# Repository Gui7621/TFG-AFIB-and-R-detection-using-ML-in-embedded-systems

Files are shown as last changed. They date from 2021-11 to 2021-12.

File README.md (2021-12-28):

# AFIB And SR Detection Using ML In Embedded Systemns

<p align="center"> 
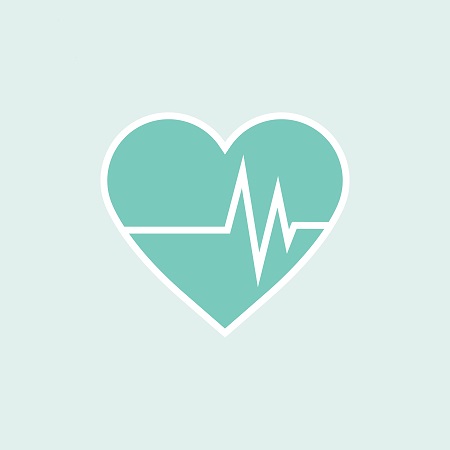
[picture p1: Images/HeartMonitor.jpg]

</p>

The project data shared in this repository has been divided into certain folders that involve different steps performed in TFG.

The first one (R Peak Detection Algorithm) has the Python file of the algorithm built along with the tests done to attest to its functionality.

The second folder (Schematic file in Fritzing) has the file to be edited in Fritzing with the schematic on the protoboard of the assembled prototype.

The "Jupyter Notebook Files" folder contains several Python files that show the entire development of the machine learning project, from working with the database including filtering and normalizing records to building and testing the neural model.

The folder "Model classifications for ECG data sampled in SimMan Simulator" contains the Excel files containing the results of the model classifications for the exams performed in SimMan.

The folder "ECG data sampled in SimMan Simulator" has some Excel files that contain RS and FA ECG records collected from SimMan, where some were used to test the model in Jupyter Notebook files.

The sixth folder (Link of the project with the final model in Edge Impulse) contains a txt file with the link to the public project in Edge Impulse that has the neural model used to make the inference in ESP32. There you can also check the model's training and test results, as well as its input data, which are precisely the individual heartbeats.

Finally, the "Program in C++" folder has the .ino file of the final program used to make the inference of the model in C++ in ESP32, including all steps of sampling the cardiac signal, data processing, obtaining the R peaks and the individual heartbeats to the final 10s model and exam scores.

<p align="center"> 
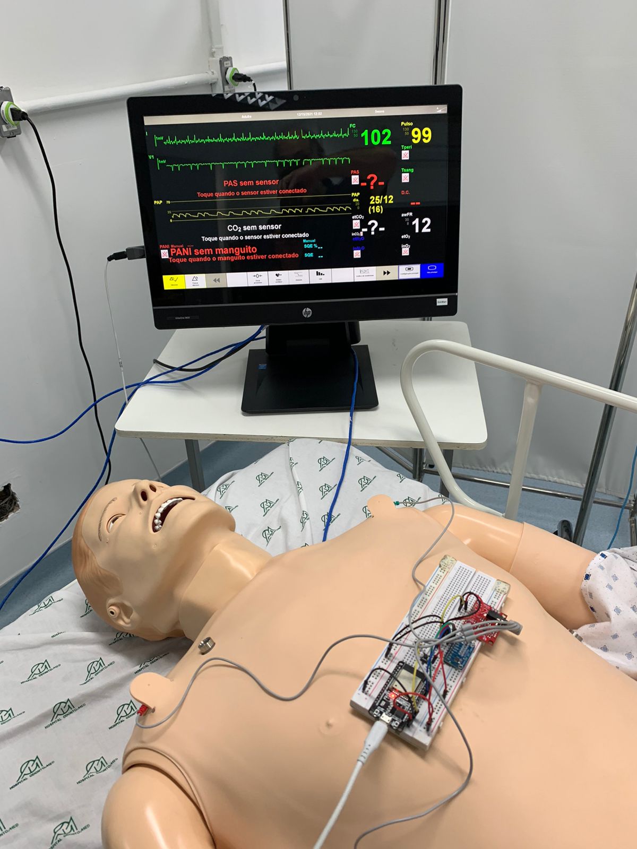
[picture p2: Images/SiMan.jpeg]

</p>

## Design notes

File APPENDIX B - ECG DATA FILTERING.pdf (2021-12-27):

## APPENDIX B - ECG DATA FILTERING

An ECG signal is made up of several sources. Recording is done using electrodes on the skin, which capture more than just the electrical activity of the heart. The primary electrical components captured are signals from the myocardium, muscles, skin-electrode interface and external interference.

The most common frequencies of important components on the ECG are:

Heart rate: 0.67 - 5 Hz (which equates to: 40 - 300 bpm)

P wave: 0,67 - 5 Hz

QRS: 10 - 30 Hz

T wave: 1 - 7 Hz

Meanwhile, the common frequencies of the medical apparatus and noise on the ECG are:

Muscle movement: 5 - 50 Hz

Respiration: 0,12 - 0,5 Hz (eg, 8 - 30 bpm)

Power line interference: 50 or 60 Hz

Other electrical: typically > 10 Hz (derived from muscle stimulators, strong magnetic fields and pacemakers with impedance monitoring)

When filtering out any biomedical signal, care must be taken not to alter the desired information in any way.

A big concern is how the QRS complex influences the filter's output; for the filter, it often represents a big unwanted boost. The possible distortion caused by the filter must be carefully quantified.

Filtering on an ECG, in principle, can be done in two steps, that is, with the application of 2 filters: a high-pass filter and a low-pass filter. The high-pass filter removes low-frequency signals (that is, only the highest frequencies can pass), and the low-pass filters remove highfrequency signals. High-pass and low-pass filters together are known as a band-pass filter, literally allowing only a certain frequency band to pass.

All filters introduce distortion into the resulting output signal. This distortion can be in amplitude or phase. Filters found in heart monitors need to be real-time and therefore cannot tolerate delays. Because of this, the filter output exhibits non-linear characteristics due to its shorter required delays. Basically, they distort different frequencies, causing phase distortion. If filters were applied during post-processing, where real-time output of the signal is unnecessary, the design of these filters can be linear, which minimizes phase distortion.

Low-pass filters on the ECG are used to remove high frequency muscle noise and especially electrical line interference noise. Analog low-pass filtering has a noticeable effect on the QRS complex, epsilon, and J waves, but does not alter the repolarization signals.

High-pass filters remove low-frequency components such as motion noise, breathing variation, and baseline wobble. Unlike low-pass filters, analog high-pass filters do not attenuate the signal too much. However, analog high-pass filters suffer from the phase shift that affects the first 5 to 10 harmonics of the signal. This means that a 0.5 Hz high-pass filter, which is a lower frequency than that produced by the myocardium, can still affect frequencies up to 5 Hz. To reduce this effect, a higher order filter is used, where frequencies near and above the cutoff frequency have virtually no attenuation.

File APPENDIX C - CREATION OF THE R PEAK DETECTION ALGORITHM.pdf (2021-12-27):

## APPENDIX C - CREATION OF THE R PEAK DETECTION ALGORITHM

An important detail in the creation of this algorithm was the fact that it did not need to operate in real time, that is, the R peaks were identified during the ECG measurement. This happens because, since the classification of the machine learning model and generation of images of heartbeats requires that the signal is already ready, this can also be done with the algorithm. This algorithm is used both in the preparation of the signal for training the model, as well as in the microcontroller for the functioning of the prototype.

With that, the algorithm works as follows: Considering that the ECG record is sampled at 100Hz for 10s, which is the standard adopted by the German database, firstly, the highest value of the 1000 points that exist in the record is found. Then, the reference value of the algorithm is assigned as being half of the highest value found previously. The functioning of this assignment directly depends on the filtering performed in the previous step, as it will be possible to remove certain noisy components that distort the signal and make it oscillate, mainly baseband noise. With filtering, the record is approximately centered at 0 and with R peaks with similar amplitudes.

In this way, all the points of the signal in question are traversed, and if any of them is greater than the calculated reference value, the next step in the algorithm is evaluated, where the 5 points following the one identified as being greater are evaluated. than the reference value, and then determine which is the greater among them. This will correspond to an R peak. It then saves both the sample value of this R peak as well as the position of this sample in the signal as a whole.

The reason for evaluating the additional 5 points is to ensure that you get the highest value of the QRS complex according to the 100Hz sampling frequency used. As one can have values greater than the reference value within the QRS complex after the R peak, it is necessary to skip a certain number of samples after its identification. Knowing that heart rate varies within a range of 40 bpm to 200 bpm, it is possible to calculate the maximum number of samples without the occurrence of an R peak as a function of frequency, given by: :

6

2 = 6∗1

2 =
30. Therefore, once an R peak is found, 30 samples of signal analysis can be skipped without

the possibility of identifying another R peak. This process is carried out during the entire length of the signal.

Consequently, it is concluded that the R peak detection algorithm needs to have the signal already sampled. Its operation consists of traversing the 10s ECG record, looking for points above a reference value within a certain range, where the largest sample in this region is an R peak. The algorithm, when tested, showed a huge efficiency when compared to the application of other similar methods, in addition to providing faster execution.

The tests that were carried out in order to verify the performance of the algorithm consisted of comparing the results obtained by the algorithm created from the signals captured from the SimMan simulator with the results considering the same input signals using a Python extension tool known as BioSPPy, which can be accessed from the following link: https://github.com/PIA-Group/BioSPPy.

This extension brings together several signal processing and pattern recognition methods aimed at analyzing biosignals, having support for several biological signals such as ECG, EEG, EMG and respiration. Its operation includes several tried and tested signal analysis techniques such as filtering, frequency analysis and R peak detection, which in turn was created from the
study of P.S. Hamilton in the article “Open Source ECG Analysis Software Documentation”.

As for the test itself, four base signals were used, composed of ECG recordings with SR with and without noise and in an analogous way for AFIB. By applying the BioSPPy algorithm, a total of 337 R peaks were detected.

After that, running the algorithm created in this article, the detection of each of the 337 R peaks identified in the previous algorithm was observed, as well as some extra indications in the AFIB signals, where when visually verifying the signal actually consisted of R peaks.

Therefore, the created algorithm was able to correctly identify the R peaks of SR and AFIB signals in comparison with the BioSPPy algorithm, as well as finding R peaks in AFIB signals that went unnoticed by the reference algorithm.

The tests and their results can be accessed in the project repository, more specifically, in the folder reserved for the development of this algorithm.

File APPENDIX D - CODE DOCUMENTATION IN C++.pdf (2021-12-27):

## APPENDIX D - CODE DOCUMENTATION IN C++

Code development in C++:

For the development of the embedded code, we wanted to reapply all the steps carried out in the training of the model written in Python, as this is extremely important for the model to be able to perform well and work under the same conditions in which it was created and trained;

In this way, the code development in C++ was divided into steps that would make the work easier and could help maintain the same conditions that were applied at a high level with Python. The chosen steps were then: data acquisition and data processing in real time, separation of beats, introduction of the signal in the model and classification. All these steps will be opened and worked on below.

Acquisition and training of data in real time:

In the acquisition step, the Adafruit_ADS1x15 library was used to configure and read the ADC, where 3 interrupts were used to manage the code's operation. The first interrupt monitored the change in a push button, and triggers a debounce routine to confirm that the switch was pressed. Then, two interrupts were triggered, in which one is triggered every 0.01s and is responsible for releasing the data acquisition flag and keeping the sampling frequency at 100 Hz, and a second interrupt is responsible for signaling the end of the data acquisition time which is 10s.

In the data processing process in Python, the library used was scipy, so that in Python two filters were defined: a high-pass with a cut-off frequency of 0.5 Hz and a low-pass with a cutoff frequency of 41 Hz In order to replicate data processing in C++, the libfilter library was used, which has very similar implementations to those used in the process carried out at a high level for model training, where this library enabled the creation of a low-pass filter of 3rd order with a cutoff frequency of 41 Hz, and a 2nd order high pass filter with a cutoff frequency of 0.5 Hz, thus forming a bandpass filter that is applied in real time as the data is acquired from the ADC.

All read and processed data were stored in an array declared as static in the microcontroller's memory that is created at the time of processor initialization. These data were stored to be used in the following steps, for the creation of data that are delivered with the objective that the classification of the model is carried out.

Separation of heartbeats:

In the step of separating the heartbeats in Python, the biosppy library was used to normalize the heartbeats and create the images, where at first we tried to make a direct translation of this library to C++, which was not very practical, leading to the creation of our own code for peak detection that was first applied in Python and then translated to C++, so with a few minor adaptations this routine managed to be translated and tested inside the microcontroller.

After all the signal peaks are identified, it goes to the heartbeat separation step. With the QRS point indices in hand, it is possible to assemble a matrix containing all the heartbeats present in the signal, taking 60 points in front of the QRS peak and 40 points behind the QRS peak, thus forming the heartbeats. Here, care is only taken to avoid picking up points that were on the edge of the signal, which can configure signals without correct identification.

Input of the signal in the model and final classification:

In this step, the deployment is carried out using the Edge Impulse tool, which was responsible for optimizing and converting the model, thus reducing both the memory expenditure used by the model and the processing expenditure necessary for it to be able to run on a processor with fewer resources, such as embedded processors. In exchange for that, the model loses some of its precision, which in the case of this project proved to be imperceptible.

After processing the model by the tool, a library is obtained with the model application ready, where both the model and some tools that were also delivered by Edge Impulse are extracted, such as the feature vector where the data that will be processed is introduced. by the model. With this in mind, we went through the classification stage, where the valid heartbeats were introduced in the features vector provided by the Edge Impulse library.

From there, the classification function is called, which will analyze and classify each heartbeat individually, so that after classifying all the beats, a comparison is made between the number of heartbeats classified as AFIB and SR. The one with the highest number of ratings is indicated as the heart rhythm identified in the 10s exam.

Trobleshoot:

Possible improvements of the work carried out would be: improvement in the quality of the filters performed, creation of a model capable of detecting a greater number of arrhythmias, in addition to an increase in the sampling rate, which would make it possible to acquire more accurate data with a smaller spacing between samples.

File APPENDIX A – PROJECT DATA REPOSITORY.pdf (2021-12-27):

## APPENDIX A – PROJECT DATA REPOSITORY

The link to the repository that contains the Jupyter Notebook programs with the functions described in this article, along with the neural model developed on the Edge Impulse platform, as well as the ECG data obtained from the measurements on the simulator SimMan is given by:

https://github.com/Gui7621/TFG-AFIB_and_SR_detection_using_ML_in_embedded_systems

In addition, the adapted database from the original German PTB-XL database is also made available, where only data related to normal sinus rhythm and atrial fibrillation were filtered. This database, which was used as a reference in the programs created in Python, can be accessed through the following link:

https://zenodo.org/record/5711347#.YZa1c07MLIW

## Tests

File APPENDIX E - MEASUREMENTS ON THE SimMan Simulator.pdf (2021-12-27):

## APPENDIX E - MEASUREMENTS ON THE SimMan SIMULATOR

The prototype developed to carry out measurements on the simulator is composed of the following components:

a) ESP32:

Development board with 30 pins of which 25 are digital input/output, Clock up to 240MHz, 520KB RAM memory and 4MB FLASH memory.

b) AD8232 cardiac monitoring sensor:

Capable of measuring the electrical activity of the heart which can be mapped as an ECG and generated as an analog reading. This sensor performs a pre-filtering in order to clean the signal from possible noise.

c) Cable with electrode pads.

They are used to connect the electrodes to the AD8232 sensor.

d) ECG electrodes with a disposable surface.

These are the devices that connect the patient with the cardiac sensor, where electrical information is obtained for printing and analyzing the ECG.

e) Protoboard and jumpers.

They carry out the electrical connections of the prototype components.

f) USB cable type A-B:

It has the function of connecting the computer with a digital output from ESP32, in order to allow the sending of data worked on the development board to the computer for future analysis.

g) ADS1115 analog-digital converter:

Its purpose is to convert the analog signal from the heart monitor to digital in order to be treated by ESP32. It has 16-bit precision at 860 samples/second. Its interface is via I2C protocol. Furthermore, it can be configured as 4 single-ended input channels or two differential channels. Its use in the prototype was necessary because the ESP32's A/D converter does not have the required quality expected for sampling and analog signal conversion.

h) Tactile key with 4 terminals:

Its function is to indicate the start of recording an exam when it is pressed. It works by sending to a digital pin of ESP32 a logic state that indicates whether it was pressed or not. The debounce technique was used in order to avoid possible problems with undefined transitions in moments of pressure due to mechanical or physical failures.

The main connections between the components listed above are described below:

Connecting the AD8232 heart monitor to the ADS1115:

Table I – AD8232 Heart Monitor Connections with ADS1115 Component

Pin name on AD8232 board | Pin functions | Connection on ADS1115
GND | Ground | Ground
3.3V | 3.3V power | 3.3V
OUTPUT | output analog signal | A0 pin
LO - | lead detection - | NC
LO + | lead detection + | NC
SDN | turn off | NC

Connection of ADS1115 analog-digital converter with ESP32:

Table II – ADS1115 Analog-to-Digital Converter Connections with ESP32

ADS1115 | Connection on ESP32
GND | Ground
3.3V | 3.3V
SCL | SCL pin (22)
SDA | DAS pin (21)
ADDR | Ground
ALRT | NC
A0 | NC
A1 | NC
A2 | NC
A3 | NC

The schematic with the connection between the three components mentioned above is shown below:

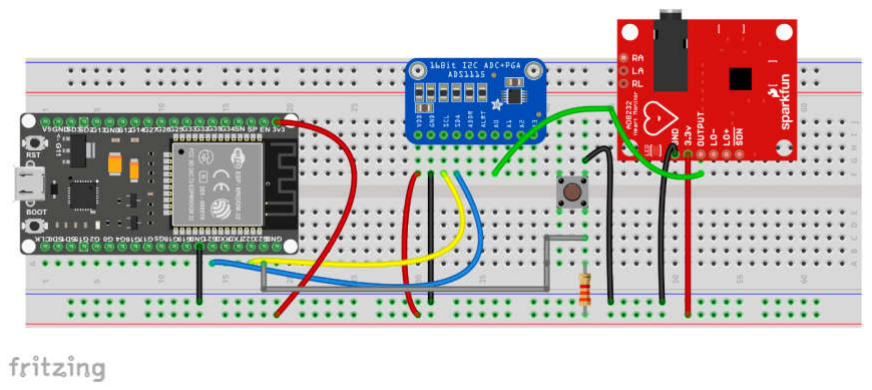
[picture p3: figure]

Fig. 1: Prototype assembly schematic. Source: Fritzing, 2021.

The connection of the electrode pads with the signals to be sampled from the body according to the type I lead is given by:

Table III – Connections of the electrode pads to the body

Cable color | Signal
Green | LA (Left Arm)
Red | RA (Right Arm)
Yellow | RL (Right Leg)

The layout of the type I lead reading in the human body is exemplified in the image below:

Fig. 2: Positioning the electrode pads on the human body. Source: Author, 2021.

The arrangement of connections already in the simulator is shown in the figures below:

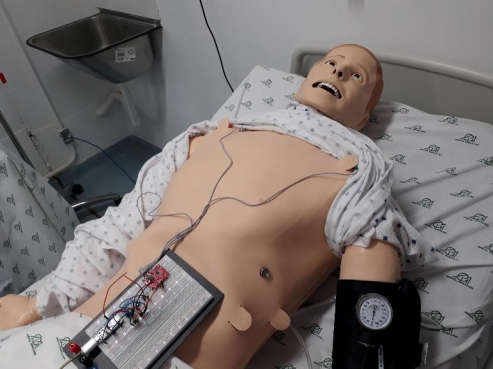
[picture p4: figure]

Fig. 3: Prototype layout in SimMan. Source: Author, 2021.

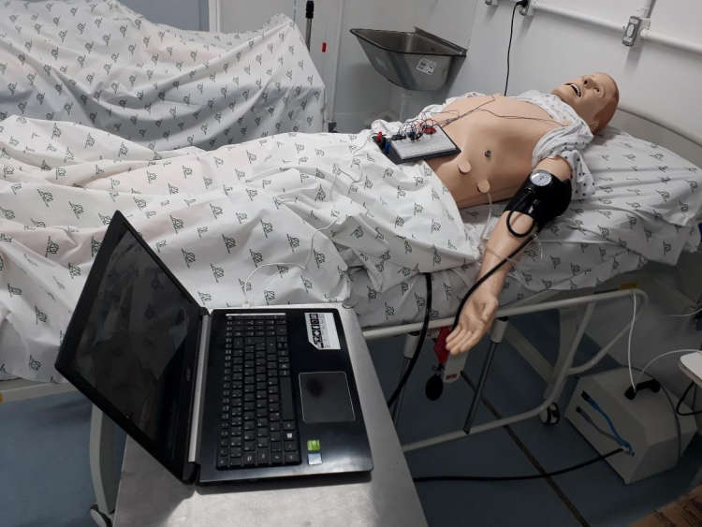
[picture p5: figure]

Fig. 4: Prototype layout in SimMan. Source: Author, 2021.

As described in the article, once the prototype had already been assembled, several AFIB and SR signals were started to be applied to the simulator, with or without noise. Shown below are some of these already filtered signals obtained.

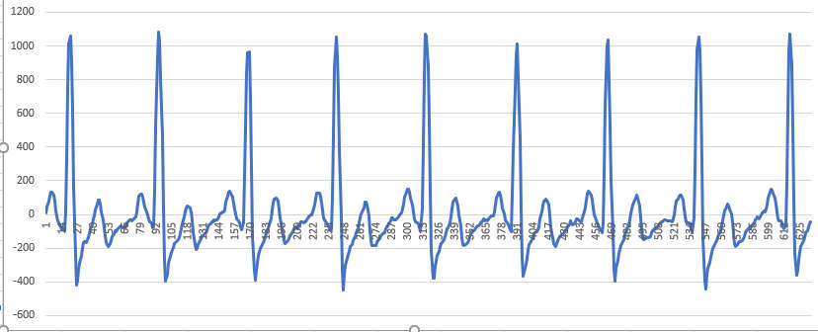
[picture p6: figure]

Fig. 5: Signal from a noiseless SR ECG record. Source: Author, 2021.

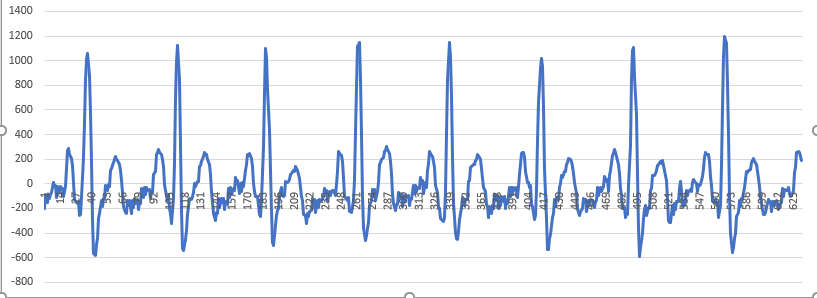
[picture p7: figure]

Fig. 6: Signal from a noisy SR ECG record. Source: Author, 2021.

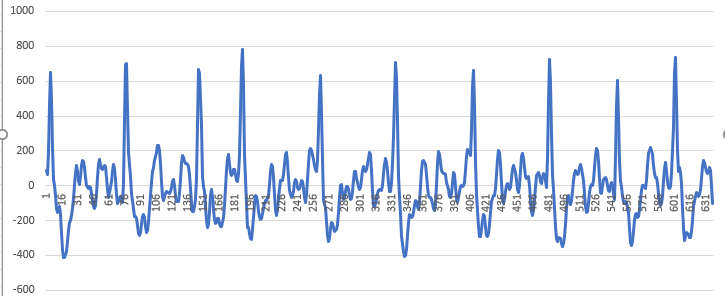
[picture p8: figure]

Fig. 7: Signal from a noiseless AFIB ECG record. Source: Author, 2021.

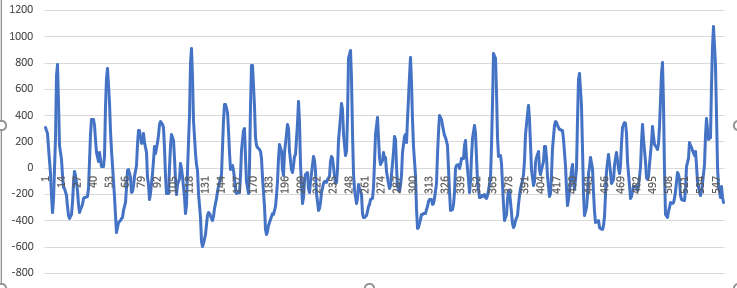
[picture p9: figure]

Fig. 8: Signal from a noisy AFIB ECG record. Source: Author, 2021.

About the classifications themselves, it is attested that they last an average of 8ms, as shown in the image below, that is, this is the duration of the model inference. This constant is close to that estimated by Edge Impulse, which was 10ms.

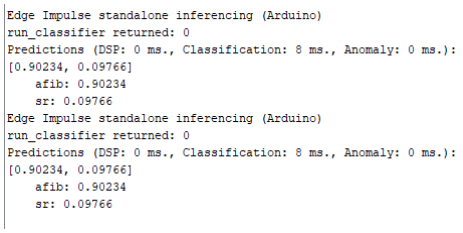
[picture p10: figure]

Fig. 9: Records of model classification parameters. Source: Author, 2021.

Finally, an idealization of how it is expected in the future to transform the prototype into a single board capable of performing both the sampling, treatment, classification and display of data and results is presented below. It will have many of the components mentioned above for the construction of the original prototype with the addition of the display, although the ESP32 will be replaced by a microcontroller with an even smaller size, containing just what is necessary to run the machine learning model and treatment of the ECG data. There is also the addition of an external battery, in order to make the ECG measurement safer, since it will not be necessary to connect directly to the electrical network.

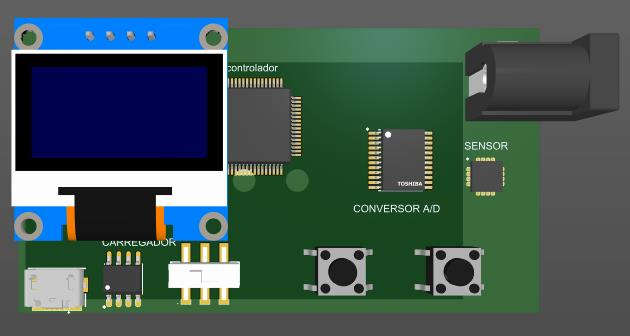
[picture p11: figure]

Fig. 10: Idealization of the final prototype of the project (front of the board). Source: Author, 2021.

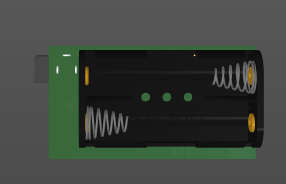
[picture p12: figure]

Fig. 11: Idealization of the final prototype of the project (behind the board). Source: Author, 2021.

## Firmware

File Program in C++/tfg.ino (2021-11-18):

/***********************************************
  Includes.
***********************************************/
#include <Adafruit_ADS1X15.h>
#include <Wire.h>
#include <movingAvg.h>
#include <filters.h>
#include <filters_defs.h>
#include <stdio.h>
#include <stdlib.h>
#include <stdint.h>
#include <ecg_project_test_1_inferencing.h>


/***********************************************
  Defines.
***********************************************/
#define SAMPLE_RATE_US 10000 //Limitado a 128 pela biblioteca Adafruit_ADS1X15 para alterar use a fução ConfigSampleRate(uint rate) com os valores disponíveis no enum sampleRate.
#define DEBOUNCE_TIME_MS 25
#define MULTIPLIER_VALUE 0.1875F
#define MOVING_AVG_WINDOW_SIZE 3
#define BUTTON_PIN 2
#define EXAM_DURATION_US 1000
#define MAX_SIGNAL_POINTS 1000
#define MAX_HEARTBEATS_CAPTURED 15
#define MAX_HEARTBEAT_IMAGE_SIZE 100
/***********************************************
  Variáveis.
***********************************************/
//Variáveis do Timer de leitura do ADC.
volatile bool timerFlagAdc;
hw_timer_t * timer0 = NULL;
portMUX_TYPE timerMux0 = portMUX_INITIALIZER_UNLOCKED;

//Variáveis do Timer de controle do tempo do exame.
volatile bool timerFlagExamFinished;
volatile int count;    // Trigger
hw_timer_t * timer1 = NULL;
portMUX_TYPE timerMux1 = portMUX_INITIALIZER_UNLOCKED;

//Variáveis dos Filtros
const float samplingTime = 0.01;                            //Sampling time em segundos.
const float cutoffFreqHigh   = 0.5;                                              //Frequência de corte em Hz.
const float cutoffFreqLow   = 41.0;                                              //Frequência de corte em Hz.
Filter fhp(cutoffFreqHigh, samplingTime, IIR::ORDER::OD2, IIR::TYPE::HIGHPASS);
IIR::ORDER  order_low  = IIR::ORDER::OD3;                                           // Order (OD1 to OD4)
Filter f(cutoffFreqLow, samplingTime, order_low);
movingAvg avgValue(1);
const float multiplier = 0.1875F;

//Variáveis do ADC.
Adafruit_ADS1115 ads;
enum sampleRate {
  SPS8 = 0x0000, //< 8 amostras por segundo.
  SPS16 = 0x0020, //< 16 amostras por segundo.
  SPS32 = 0x0040, //< 32 amostras por segundo.
  SPS64 = 0x0060, //< 64 amostras por segundo.
  SPS128 = 0x0080, //< 128 amostras por segundo(padrão).
  SPS250 = 0x00A0, //< 250 samples amostras por segundo.
  SPS475 = 0x00C0, //< 475 amostras por segundo.
  SPS860 = 0x00E0, //< 860 amostras por segundo.
};

//Variáveis do Botão.
const uint button = BUTTON_PIN;         //Botão configurado no pino2.
volatile boolean buttonFlag;

//Variáveis para a criação de HeartBeats.
int SignalFiltred[MAX_SIGNAL_POINTS];
int SignalImages[MAX_HEARTBEATS_CAPTURED][MAX_HEARTBEAT_IMAGE_SIZE];
float SignalImagesNormalized[MAX_HEARTBEATS_CAPTURED][MAX_HEARTBEAT_IMAGE_SIZE];
int SignalMaxPointsIndex[MAX_SIGNAL_POINTS];
int signalIndex;

//Variáveis para controle da máquina de estados.
uint state = 1;
bool examStart;
enum states {ms_wait, ms_readingButton, ms_automaticInitiation, ms_starting, ms_collectingData, ms_examFinished, ms_buldingImage, ms_sendingImageToClassification};

//Variáveis para classificação.
static int AFIB_cont = 0;
static int SR_cont = 0;
int zeroCountClassifcationImage = 0;
static float features[100] = {
  // copy raw features here (for example from the 'Live classification' page)
  // see https://docs.edgeimpulse.com/docs/running-your-impulse-arduino
};

/***********************************************
  Definição de funções.
***********************************************/
//Funções do Timer de leitura do ADC.
void IRAM_ATTR onTimer0();

//Funções do Timer de controle do tempo do exame.
void IRAM_ATTR onTimer1();

//Fuções do ADC.
int16_t ReadADC();
void ConfigSampleRate(uint rate);

//Funções do Filtro.
float FilterSignal(int16_t adcValue, float cutoffHighPassFilter, float cutoffLowPassFilter);

//Funções do botão.
boolean Debounce(uint buttonToRead);
void ButtonInterrupt();

//Funções para a criação de HeartBeats.
float FoundSignalPeaks(int* heartSignal);
void RPeakDetection(int* heartSignal);
void ExtractHeartbeats(int sinal_imagem[MAX_HEARTBEATS_CAPTURED][MAX_HEARTBEAT_IMAGE_SIZE]);
void NormalizeHeartbeats();

//Funções para classificação.
void classification(void);
void ei_printf(const char *format, ...);
int raw_feature_get_data(size_t offset, size_t length, float *out_ptr);

/***********************************************
  Setup.
***********************************************/
void setup() {
  //Configuração Serial.
  Serial.begin(38400);
  while (!Serial)
  {

  };

  Serial.println("CLEARSHEET");
  Serial.println("CLEARDATA");
  Serial.println("LABEL,Time,Classification");

  //Configuração do ADC.
  ads.begin();
  //ConfigSampleRate(SPS128);

  //Configuração do Filtro.
  avgValue.begin();

  //Configuração do Botão.
  buttonFlag = false;
  pinMode(button, INPUT);

}

/***********************************************
  Loop.
***********************************************/
void loop() {

  switch (state) {
    case ms_readingButton:
      {
        attachInterrupt(digitalPinToInterrupt(button), ButtonInterrupt, FALLING);
        if (buttonFlag ==  true) {
          bool buttonValue = Debounce(button);
          if (buttonValue == true) {
            detachInterrupt(digitalPinToInterrupt(button));
            buttonValue = false;
            buttonFlag = false;
            examStart = true;
            state = ms_starting;
          }
          buttonFlag = false;
        }
        break;
      }
    case ms_automaticInitiation:
      {
        examStart = true;
        state = ms_starting;
        break;
      }
    case ms_starting:
      {
        if (examStart == true) {
          examStart = false;
          //delay(5000);

          //Configuração do Timer de controle do tempo do exame.
          timer1 = timerBegin(1, 80, true);  // timer 1, MWDT clock period = 12.5 ns * TIMGn_Tx_WDT_CLK_PRESCALE -> 12.5 ns * 80 -> 1000 ns = 1 us, countUp
          timerAttachInterrupt(timer1, &onTimer1, true); // edge (not level) triggered
          timerAlarmWrite(timer1, 10000000, true); // 250000 * 1 us = 250 ms, autoreload true

          //Configuração do Timer de leitura do ADC.
          timer0 = timerBegin(0, 80, true);  // timer 0, MWDT clock period = 12.5 ns * TIMGn_Tx_WDT_CLK_PRESCALE -> 12.5 ns * 80 -> 1000 ns = 1 us, countUp
          timerAttachInterrupt(timer0, &onTimer0, true); // edge (not level) triggered
          timerAlarmWrite(timer0, SAMPLE_RATE_US, true); // 2000000 * 1 us = 2 s, autoreload true

          timerAlarmEnable(timer1); // habilita timer de tempo do exame.
          timerAlarmEnable(timer0); // habilita timer de leitura de adc.

          timerFlagExamFinished = false;
          signalIndex = 0;
          state = ms_collectingData;
        } else if (examStart == false) {
          state = ms_readingButton;
        }
        break;
      }
    case ms_collectingData:
      {
        if ((timerFlagAdc == true) && (timerFlagExamFinished == false)) {
          if ((signalIndex <= 999)) {
            int leituraAdc = FilterSignal(ReadADC(), 0.5f, 41.0f);
            if (signalIndex < 10) {
              leituraAdc = 0;
            }
            SignalFiltred[signalIndex] = leituraAdc;
            signalIndex++;
            timerFlagAdc =  false;
          }
        }
        break;
      }
    case ms_examFinished:
      {
        timerFlagExamFinished = false;
        signalIndex = 0;
        state = ms_buldingImage;
        break;
      }
    case ms_buldingImage:
      {
        RPeakDetection(SignalFiltred);
        ExtractHeartbeats(SignalImages);
        NormalizeHeartbeats ();
        state = ms_sendingImageToClassification;
        break;
      }
    case ms_sendingImageToClassification:
      {
        for (int imageClassificationIndex = 0; imageClassificationIndex < MAX_HEARTBEATS_CAPTURED - 1; imageClassificationIndex++) {
          for (int i = 0; i < 100; i++) {
            if (SignalImagesNormalized[imageClassificationIndex][i] == 0) {
              zeroCountClassifcationImage++;
            }
            features[i] = SignalImagesNormalized[imageClassificationIndex][i];
          }
          if (zeroCountClassifcationImage >= 30) {
            zeroCountClassifcationImage = 0;
            continue;
          }
          else if (zeroCountClassifcationImage < 30) {
            zeroCountClassifcationImage = 0;
            classification();
          }
        }
        //Serial.print("contagem Afib: \n");
        //Serial.print(AFIB_cont);
        //Serial.print("\n");
        //Serial.print("contagem SR: \n");
        //Serial.print(SR_cont);
        //Serial.print("\n");
        if (AFIB_cont > SR_cont) {
          Serial.print("DATA,TIME,");
          Serial.println("1");
        } else if (AFIB_cont < SR_cont) {
          Serial.print("DATA,TIME,");
          Serial.println("0");
        }
        AFIB_cont = 0;
        SR_cont = 0;
        state = ms_wait;
        break;
      }
    case ms_wait:
      {
        delay(1000);
        state = ms_automaticInitiation;
          break;
      }
    default:
      state = ms_wait;
      break;
  }

}

/***********************************************
  Funções.
***********************************************/
/**

*/
void IRAM_ATTR onTimer0() {
  //portENTER_CRITICAL_ISR(&timerMux0);
  //Serial.println("Timer 0 habilita adc");
  timerFlagAdc = true;
  //portEXIT_CRITICAL_ISR(&timerMux0);
}

/**

*/
void IRAM_ATTR onTimer1() {
  portENTER_CRITICAL_ISR(&timerMux1);
  timerAlarmDisable(timer0); // desabilita timer de leitura de adc.
  //count++;
  //if (count >= 100) {
  //Serial.println("Timer 1 finaliza exame");
  timerFlagExamFinished = true;

  timerAlarmDisable(timer1); // desabilita timer de tempo do exame.
  state = ms_examFinished;
  //}
  portEXIT_CRITICAL_ISR(&timerMux1);
}

/**

*/
int16_t ReadADC() {
  int16_t adc0;
  adc0 = ads.readADC_SingleEnded(0);

  //Printa o valor lido no adc no monitor serial.
  //Serial.print("AIN0: "); Serial.println(adc0);

  return adc0;
}

/**

*/
void ConfigSampleRate(uint rate) {
  ads.setDataRate(rate);
}

/**

*/
float FilterSignal(int16_t adcValue, float cutoffHighPassFilter, float cutoffLowPassFilter) {

  float filteredVal = f.filterIn(adcValue * multiplier);
  float finalFilteredVal = fhp.filterIn(filteredVal);
  int avg = avgValue.reading(finalFilteredVal);

  //Printa o valor lido no adc no monitor serial.
  //Serial.print("Valor filtrado: "); Serial.println(final_filteredval);

  return avg;
}

/**

*/
boolean Debounce(uint buttonToRead) {
  volatile bool valueRead = !digitalRead(buttonToRead);
  unsigned long lastDebounceTime = millis();
  while (1) {
    if ((millis() - lastDebounceTime) > DEBOUNCE_TIME_MS) {
      if (valueRead == !digitalRead(buttonToRead)) {
        return valueRead;
      }
      else {
        return false;
      }
    }
  }
}

/**

*/
void ButtonInterrupt() {
  buttonFlag = true;
}

/**

*/
float FoundSignalPeaks(int* heartSignal) {
  int biggerValue = 0;
  int smallerValue = 1000000;
  for (uint i = 0; i < MAX_SIGNAL_POINTS - 1; i++) {
    if (heartSignal[i] > biggerValue) {
      biggerValue = heartSignal[i];
    }
    if (heartSignal[i] < smallerValue) {
      smallerValue = heartSignal[i];
    }
  }
  //Serial.print("Maior valor: "); Serial.println(biggerValue);
  //Serial.print("Menor valor: "); Serial.println(smallerValue);
  return biggerValue;
}

/**
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

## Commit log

2021-11-17 adicionada nova pasta de teste
2021-11-18 Adding the required files
    [afib_sem_ruido_database_1.xlsx, afib_sem_ruido_database_2.xlsx, afib_sem_ruido_database_3.xlsx, afib_sem_ruido_final.xlsx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]
2021-11-18 Adding the arduino file
2021-11-19 adding a schematic file
    [TFG-ECG.fzz]
2021-12-27 Csv files added
    [ecg_data_boneco_afib_com_ruido.csv, ecg_data_boneco_afib_com_ruido.xlsx, ecg_data_boneco_afib_sem_ruido.csv, ecg_data_boneco_afib_sem_ruido.xlsx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]
2021-12-27 Folder's names changed
    [TFG-ECG.fzz, afib_sem_ruido_database_1.xlsx, afib_sem_ruido_database_2.xlsx, afib_sem_ruido_database_3.xlsx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]
